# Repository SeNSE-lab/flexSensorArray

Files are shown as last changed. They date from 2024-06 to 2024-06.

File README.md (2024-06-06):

# flexSensorArray
whisking

# Software
Check scripts for the majority of the documentation. 3 scrips are included here:
- **flexSensorArray_control.ino** firmware to be loaded onto an Arduino Mega
- **flexlib.py**  python library that provides an api to control the flex sensor array and read signals. 
designed to be imported into an ipython notebook
- **controller_notebook.ipynb** notebook used to control the experiment. contains examples for using the flex
sensor array. designed to be the software interface for the project

## Arduino Software
It is recommended to install Arduino IDE 2 on your machine, install required 
libraries with the Arduino Library Manager, then upload the flexSensorArray_control.ino 
onto your Arduino Mega  

You should not need to do anything besides load the flexSensorArray_control.ino 
onto your Arduino. The only change to the code I might suggest is to 
reduce the baud rate if you're encountering too many communication errors. Make sure to edit the BAUD_RATE 
in the flexlib file to match if you do  

### Additional Required Libraries
These should all be available in the Arduino Library Manager
- Adafruit_MotorShield
- TimerOne
- AccelStepper

## Python
controller_notebook is designed to be the interface with this project, and 
ideally is the only file that should be edited. You will need to use a local notebook
(i.e. not colab, jupyter notebook recommended) as communication with the Arduino 
occurs via serial.

### Additional Required Libraries
- pyserial
- pandas
- matplotlib (optional but recommended)

# Hardware
## Parts
- Arduino Mega
- [Adafruit Motor Shield V2](https://learn.adafruit.com/adafruit-motor-shield-v2-for-arduino/overview)  and header pins
- 3.3 V, 1.5 or 3 Amp power supply (for 1 or 2 motors respectively)
- [Stepper motor](https://www.moonsindustries.com/p/nema-17-standard-hybrid-stepper-motors/ms17hd6p4150-000004611110008904)
- [Motor shaft coupler](https://www.amazon.com/QCQIANG-Coupling-Coupler-Flanged-Handmade/dp/B09TQM6F17?th=1)
- [Limit switch](https://www.digikey.com/en/products/detail/omron-electronics-inc-emc-div/D2FS-FL-N/4753388)
- [Flex sensor](https://www.adafruit.com/product/1070)
- [Flex sensor clincher connector](https://www.sparkfun.com/products/14195)
- 3D printed whisker
- 3D printed 2-sided whisker bracket
- 3D printed homing tab
- 3D printed motor mount
- ~100 kOhm resistor
- M3 harware
- Various wires and breadboard

## Microcontroller and Motorshield
This project was designed to be run on an Arduino Mega and use
[Adafruit Motorshields V2](https://learn.adafruit.com/adafruit-motor-shield-v2-for-arduino/overview) 
If you are stacking shields, make sure to solder the address bits. When initializing software, pass in 
the integer value of the address pins soldered (e.g. if you solder the two rightmost pins, 
the address would be 3 - 00011 in binary).

Each Arduino can support up to 16 whiskers and up to 16 stacked shields (though only up to a few shields are 
expected to be used). Each shield can support up to 2 stepper motors. 

## Power
The [stepper motors](https://www.moonsindustries.com/p/nema-17-standard-hybrid-stepper-motors/ms17hd6p4150-000004611110008904)
provided are rated for 1.5 amps, and the coils have a resistance of 2.2 ohms. Thus, a 3.3 V power supply 
that can provide 3 amps is recommended if you plan to run 2 motors on one motor shield.
3 amps is also the limit for the motor shields. Be careful of motors overheating and chips on the 
motor shield burning out if you go above 3.3 volts. You can plug power into the Arduino barrel jack 
and put the power jumper on the shield, or hook up power to the power terminal on the motor shield.  

## Wiring
### Arduino and Motor Shield
The Arduino pictured below is wired for 2 motors with 2 whiskers each. Note the order of the colored wires 
connected to the motor shield motor terminals. Whisker outputs should be wired in the order you wish 
them to be referenced starting at A0. Limit pins should be connected in the even numbered pins starting 
at 22. Make sure these are wired in the same order that you initialize the motors. For example, if your 
motor string is '21' and you have 2 whiskers per column, plug the limit pin associated with the
motor connected to second stepper terminal
(M3 and M4) into pin 22 and the limit pin associated with the motor in the first stepper terminal 
to pin 24. Then hook up the whiskers on stepper 2 to A0 and A1 and the whiskers on stepper 1 
to A2 and A3.

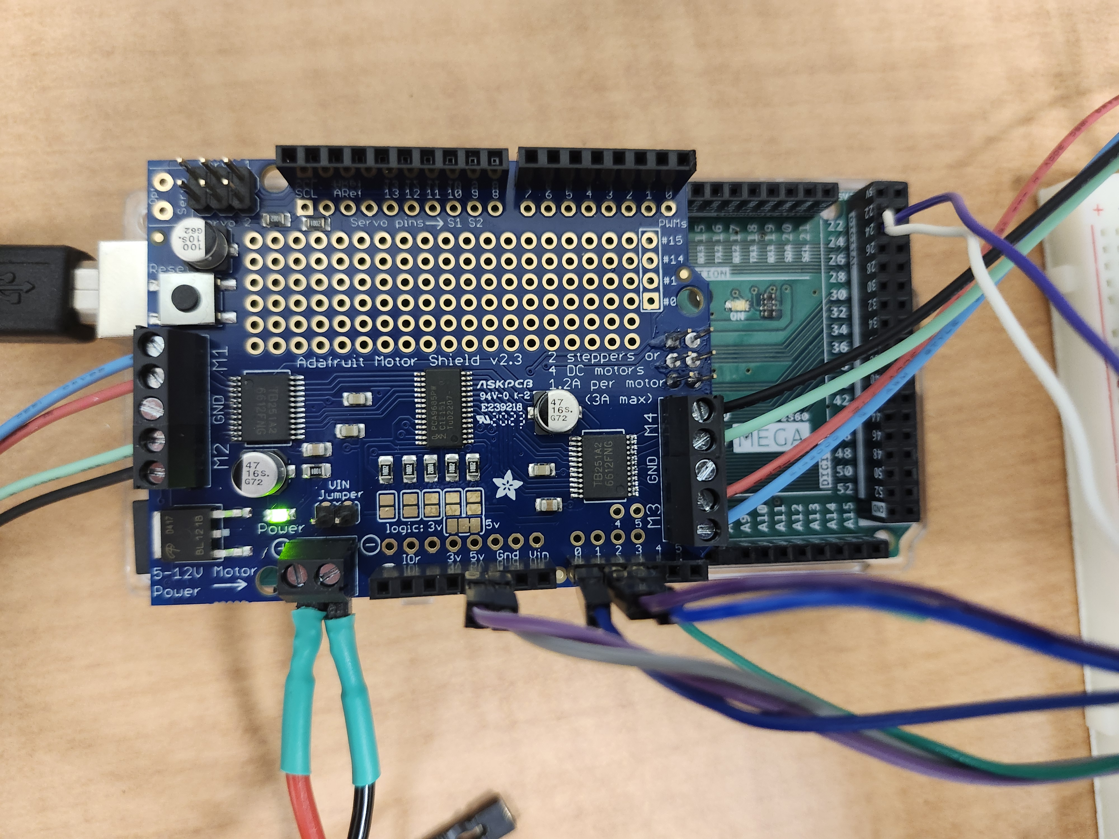
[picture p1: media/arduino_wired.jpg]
arduino_wired


### Whiskers
This project is designed to use a voltage divider circuit to read the signals from the whiskers. 
Wire a resistor between +5V and one end of your whisker sensor. This is your output, also wire it to 
one of the analog pins on the arduino. Wire the other end of the whisker sensor to ground. It may take 
some tuning to figure out the best resistor value to use to get the best signal range without saturating 
the signal. I found around 100 kOhms to be a good value (I used 2 200 kOhm resistors in parallel). 
The flex sensor resistance is about 25 kOhms at rest with resistance increasing as it bends. Note 
that the Arduino is using a reference voltage of 1.1 V for reading the analog signal, so you do not 
want your output voltage to go above 1.1 V.

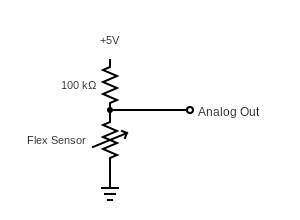
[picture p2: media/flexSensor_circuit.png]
flexSensor_circuit


### Limit Switch
As there is no encoder on the stepper motor, the limit switch is used to find the home/0 steps position of 
the motor. During the homing procedure (which runs during the MotorController.init() function) the stepper 
will rotate until the limit tab triggers the limit switch, then record this position as 0 steps.

The two pins closest to the green button/lever hinge are the active pins on the limit switch. One should 
be wired to one of the even numbered pins starting at 22 on the Arduino, and the other to ground.  

Note that there are two places you may place the limit switch on the 3D printed limit switch holder. One 
is designed to trigger when the whiskers are at "-90°", or parallel to 2 sides of the square motor. The 
other is 72° away from this. Chose whichever best fits your needs, but the default control parameters were 
chosen when using the "72°" slot as shown below.

## Assembly of other components
Image of assembled whisker column:
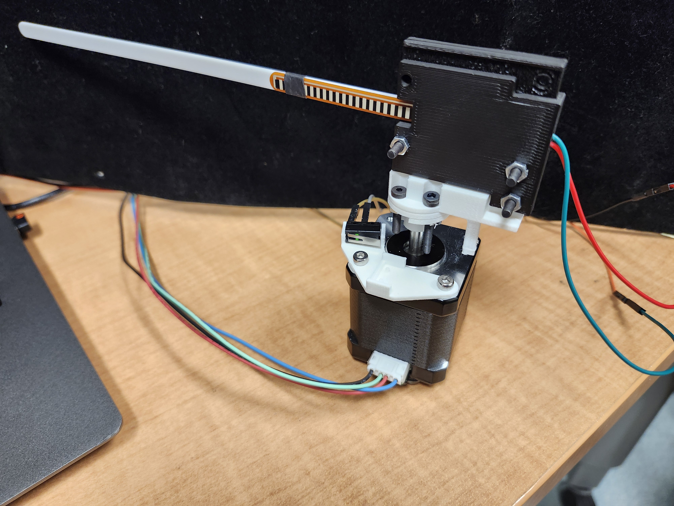
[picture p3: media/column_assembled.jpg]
column_assembled


A few tips:
- All hardware components use M3 screws
- A screw can be removed from the motor housing to allow for the screws holding the limit switch 
holder to be screwed in all the way
- The tip of the flex sensor should be only loosely held by a band, as it needs to slide as the whisker flexes. 
Tape the back of the band if necessary to prevent it from moving along the whisker. Some heat shrink was provided to use as 
this band, apply heat to make it tighter
- Ensure the flex sensor is straight when closing the clincher connector
- The 3D printed motor shaft couplers have a hole that allows you to use an M3 screw as a set screw. I may have made the hole diameter a bit too large
as the set screws easily strip the plastic hole. Try wedging something thin along the 
flat side of the shaft or taping the shaft to tighten the fit if this is a problem. Or try a larger diamter screw if you have one available.

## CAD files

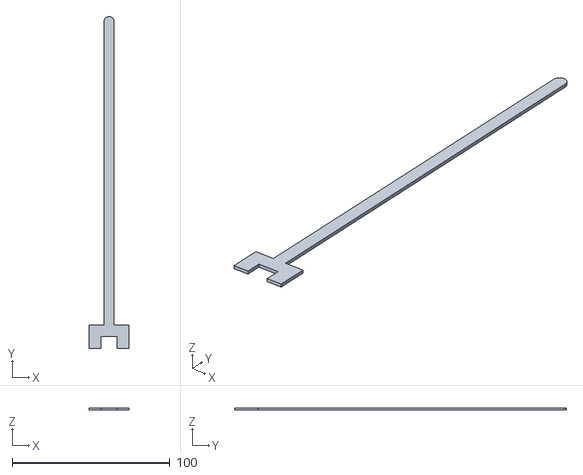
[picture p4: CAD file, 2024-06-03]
CAD/whisker.stl
25.3 x 210.5 x 1.50

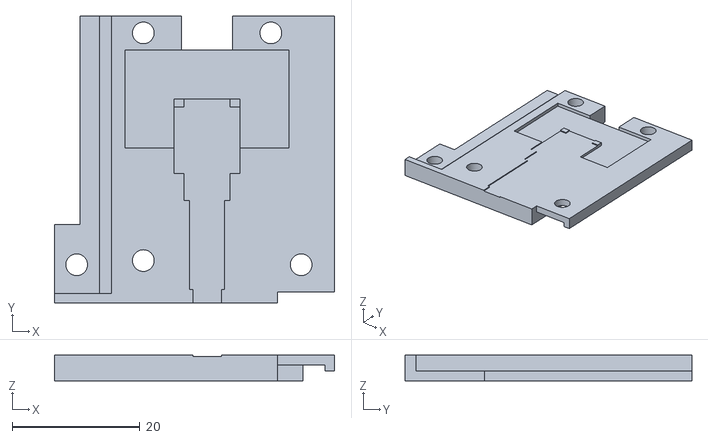
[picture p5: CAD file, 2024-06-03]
CAD/bracket_rear.stl
43.9 x 45.0 x 4.00

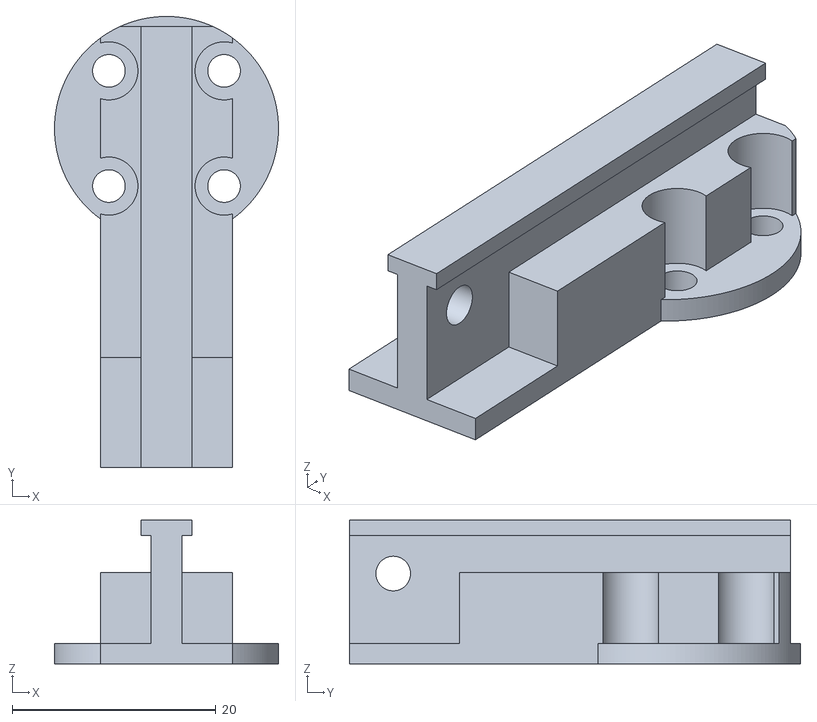
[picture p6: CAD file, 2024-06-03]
CAD/motor_mount.stl
22.0 x 44.3 x 14.1

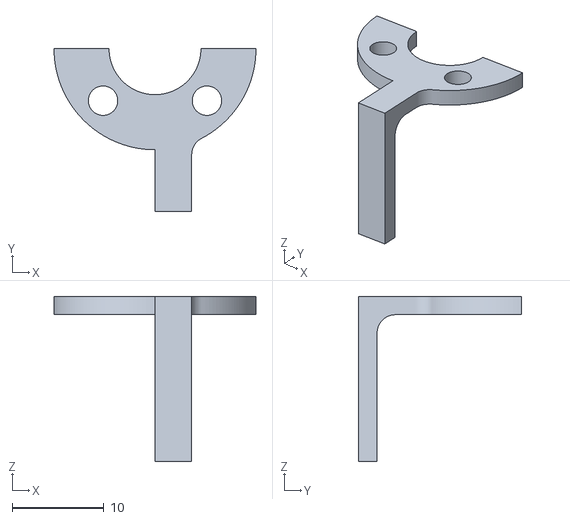
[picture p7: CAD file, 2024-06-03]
CAD/homing_limit_tab.stl
22.0 x 17.7 x 18.0

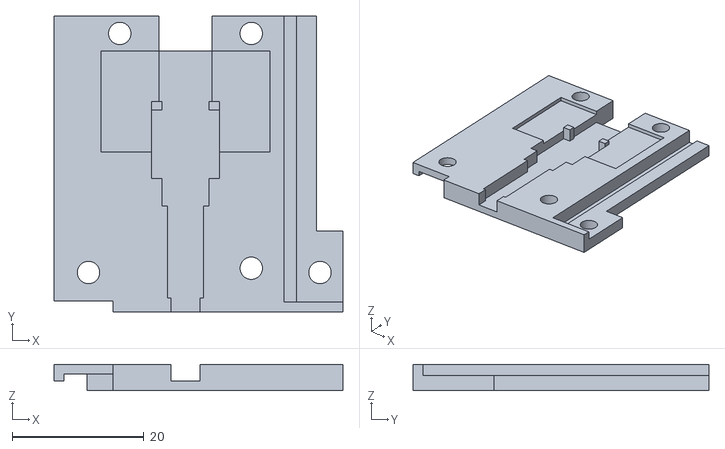
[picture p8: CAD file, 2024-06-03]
CAD/bracket_front.stl
43.9 x 45.0 x 4.00

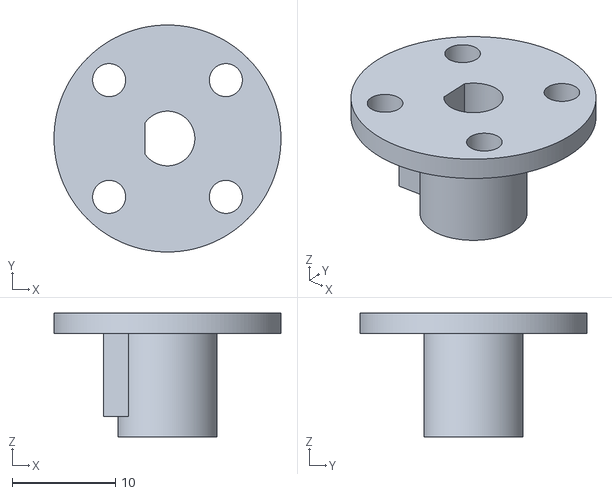
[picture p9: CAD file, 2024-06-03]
CAD/plastic_motor_coupler.stl
22.0 x 22.0 x 12.0

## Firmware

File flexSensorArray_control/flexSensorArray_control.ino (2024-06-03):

#include <Wire.h>
#include <Adafruit_MotorShield.h>
#include "utility/Adafruit_MS_PWMServoDriver.h"
#include <TimerOne.h>
#include <AccelStepper.h>

// Created by Kevin Kleczka May 2024, contact kevin.kleczka@northwestern.edu


////////// Initialize constants
// flag to denote command should be applied to all whiskers/column
#define ALL_FLAG 999

// Serial baud rate, make sure this matches with flexlib.BAUD_RATE
const unsigned long BAUD = 921600;

// Steps per revolution of motor. NOTE: since INTERLEAVE step mode is used, this is double the number of steps per revolution of the motor
const int STEPS_PER_REVOLUTION = 400;

//// hardware addresses
// These are used based on the integer value passed in
//    e.g. if no addr pins are soldered on a shield pass in 0, if the first and second from the right are soldered pass in 3
const uint8_t motorShield_addresses[] = { 0x60, 0x61, 0x62, 0x63, 0x64, 0x65, 0x66, 0x67, 0x68, 0x69, 0x6A, 0x6B, 0x6C, 0x6D,
                                          0x6E, 0x6F, 0x70, 0x71, 0x72, 0x73, 0x74, 0x75, 0x76, 0x77, 0x78, 0x79, 0x7A, 0x7B, 0x7C, 0x7D, 0x7E, 0x7F };
// these will be used in order as new whiskers and motors are added
//  e.g. if you set up 6 whiskers on 2 motors (3 whiskers each) the whisker signals will be read from A0 to A5, and limit pins will be 22 and 24
const int analogPins[] = { A0, A1, A2, A3, A4, A5, A6, A7, A8, A9, A10, A11, A12, A13, A14, A15 };
const int limit_pins[] = { 22, 24, 26, 28, 30, 32, 34, 36, 38, 40, 42, 44, 46, 48, 50, 52 };


// Maximum supported hardware
const int MAX_SHIELDS = 16;
const int MAX_STEPPERS = 16;
const int MAX_WHISKERS = 16;

// Max number of steps allowed to be targeted
const long MAX_STEPS = 200;


////////// Initialize variables
// default step mode
int step_mode = INTERLEAVE;

// pointer arrays for motor control
Adafruit_MotorShield *motor_shields[MAX_SHIELDS];
Adafruit_StepperMotor *steppers[MAX_STEPPERS];
AccelStepper *accel_steppers[MAX_STEPPERS];

// default whisk steps
long default_prot = 133;
long default_ret = 22;

// default accelStepper maxSpeed and acceleration
long default_speed = 1500;
long default_accel = 500;

// set up column parameters
long prot_steps[MAX_STEPPERS] = { default_prot };
long ret_steps[MAX_STEPPERS] = { default_ret };
int is_left[MAX_STEPPERS] = { 0 };
int whisker_col_id[MAX_WHISKERS];
int whisking_status[MAX_STEPPERS] = { 0 };

// init number of connected components
int num_shields = 0;
int num_steppers = 0;
int num_whiskers = 0;

// datastream buffer
long output_buffer[7];
int buff_idx;

// sampling params
volatile int sampling = 0;
unsigned long sampling_period = 20000;

// allocate space for a few variables
int stepper_id;
int status;

// set debug messages for serial monitor debugging
int debug = 0;

//////// Accel stepper setup variables
// I gave up trying to figure out a better way to do this
// Forward and backward stepping functions for each stepper
void forwardStep0();
void backwardStep0();
void forwardStep1();
void backwardStep1();
void forwardStep2();
void backwardStep2();
void forwardStep3();
void backwardStep3();
void forwardStep4();
void backwardStep4();
void forwardStep5();
void backwardStep5();
void forwardStep6();
void backwardStep6();
void forwardStep7();
void backwardStep7();
void forwardStep8();
void backwardStep8();
void forwardStep9();
void backwardStep9();
void forwardStep10();
void backwardStep10();
void forwardStep11();
void backwardStep11();
void forwardStep12();
void backwardStep12();
void forwardStep13();
void backwardStep13();
void forwardStep14();
void backwardStep14();
void forwardStep15();
void backwardStep15();

// Function pointers for stepping functions
typedef void (*StepFunc)();

StepFunc forwardSteps[MAX_STEPPERS];
StepFunc backwardSteps[MAX_STEPPERS];

void initializeSteppers();


//////// Set up command communication protocol
// Number of words (argument variables) in a user command line.
char *argument_words[8];
// Buffer to use for receiving special user-defined ASCII commands.
char user_command_buffer[64];
// Index to use when filling the user command buffer.
uint8_t user_command_buffer_index = 0;
uint8_t c = 0;  // character received
char output_line[71];

void parse(char *line, char **argument_words, uint8_t maxArgs) {
  uint8_t argCount = 0;
  while (*line != '\0') { /* if not the end of line ....... */
    while (*line == ',' || *line == ' ' || *line == '\t' || *line == '\n')
      *line++ = '\0';         /* replace commas and white spaces with 0    */
    *argument_words++ = line; /* save the argument position     */
    argCount++;
    if (argCount == maxArgs - 1)
      break;
    while (*line != '\0' && *line != ',' && *line != ' ' && *line != '\t' && *line != '\n')
      line++; /* skip the argument until ...    */
  }
  *argument_words = '\0'; /* mark the end of argument list  */
}


// Timer1 interrupt service routine
void timerIsr() {
  // prints the current values over serial (ie sends character representations of all values)
  // prints a line for each attached whisker with values in following order:
  //  'timestamp', 'whisker_id', 'stepper_id', 'whisking_status', 'curr_steps', 'sensor_out'
  // NOTE that the millis() interrupt gets paused during handling of this intterrupt, so all whiskers will have the same timestamp
  if (sampling) {

    for (int i = 0; i < num_whiskers; i++) {
      buff_idx = 0;
      // 'timestamp
      output_buffer[buff_idx] = millis();
      buff_idx++;
      // whisker_id
      output_buffer[buff_idx] = i;
      buff_idx++;
      //stepper_id
      stepper_id = whisker_col_id[i];
      output_buffer[buff_idx] = stepper_id;
      buff_idx++;
      // whisking_status
      output_buffer[buff_idx] = whisking_status[stepper_id];
      buff_idx++;
      // curr_steps
      output_buffer[buff_idx] = accel_steppers[stepper_id]->currentPosition();
      buff_idx++;
      // sensor_out
      output_buffer[buff_idx] = analogRead(analogPins[i]);
      buff_idx++;
      for (int j = 0; j < buff_idx; j++) {
        Serial.print(output_buffer[j]);
        Serial.print(' ');
      }
      Serial.println();
    }
  }
}

void home_stepper(int stepper_id) {
  // retract stepper until limit switch is triggered
  while (digitalRead(limit_pins[stepper_id]) == HIGH) {
    if (is_left[stepper_id]) {
      steppers[stepper_id]->onestep(FORWARD, SINGLE);
    } else {
      steppers[stepper_id]->onestep(BACKWARD, SINGLE);
    }
    delay(25);
  }
  accel_steppers[stepper_id]->setCurrentPosition(0);
}



void setup() {

  Serial.begin(BAUD);

  delay(250);

  // let python know we're running
  Serial.println('!');

  // set reference voltage for analog read to 1.1 v to maximize signal range
  analogReference(INTERNAL1V1);

  //////// read setup commands
  // separate command and inputs with spaces ("cmd val1 val2 ...")

  // add shield with steppers and whiskers
  //  s shieldAddr steppersToAdd whiskersPerStepper sideColumnIsOn
  //    for last 3 params first digit is added first, second is added second
  //    e.g. "s 0 12 22 00" adds motor shield with addr 0, adds stepper 1 with 2 whiskers on the right side, then adds stepper 2 with 2 whiskers on the right side
  // set sampling interval in microseconds
  //  p interval
  //    e.g. "p 20000" sets the sample interval to 20,000 microseconds, or 50 Hz
  // complete setup
  //  c
  //    e.g. "c" denotes the setup is complete

  int setup_complete = 0;
  int sidx;
  int midx;
  int numw;
  int side = 0;
  num_whiskers = 0;
  while (!setup_complete) {
    while (Serial.available() > 0) {  // PC communication
      c = Serial.read();
      if (c == '\r') {
        user_command_buffer[user_command_buffer_index] = 0;
        parse((char *)user_command_buffer, argument_words, sizeof(argument_words));

        // add shield with steppers and whiskers
        //  s shieldAddr steppersToAdd whiskersPerStepper sideColumnIsOn
        if (strcmp(argument_words[0], "s") == 0) {
          sidx = atoi(argument_words[1]);
          midx = atoi(argument_words[2]);
          numw = atoi(argument_words[3]);
          side = atoi(argument_words[4]);

          int mone = midx % 10;
          int mten = (midx / 10) % 10;

          int wone = numw % 10;
          int wten = (numw / 10) % 10;

          int sone = side % 10;
          int sten = (side / 10) % 10;


          motor_shields[num_shields] = new Adafruit_MotorShield(motorShield_addresses[sidx]);
          motor_shields[num_shields]->begin();

          if (mten) {
            if (wten) {
              for (int i = 0; i < wten; i++) { whisker_col_id[i] = num_steppers; }
              num_whiskers += wten;
            }
            is_left[num_steppers] = sten;
            steppers[num_steppers] = motor_shields[num_shields]->getStepper(STEPS_PER_REVOLUTION, mten);
            num_steppers += 1;
          }
          if (mone) {
            if (wone) {
              for (int i = 0; i < wone; i++) { whisker_col_id[i] = num_steppers; }
              num_whiskers += wone;
            }
            is_left[num_steppers] = sone;
            steppers[num_steppers] = motor_shields[num_shields]->getStepper(STEPS_PER_REVOLUTION, mone);
            num_steppers += 1;
          }
          num_shields += 1;
        }
        // set sampling interval in microseconds
        //  p interval
        else if (strcmp(argument_words[0], "p") == 0) {
          sampling_period = atoi(argument_words[1]);
        }
        // complete setup
        //  c
        else if (strcmp(argument_words[0], "c") == 0) {
          setup_complete = 1;
        }

        user_command_buffer_index = 0;
      } else if (((c == '\b') || (c == 0x7f)) && (user_command_buffer_index > 0)) {
        user_command_buffer_index--;
      } else if ((c >= ' ') && (user_command_buffer_index < sizeof(user_command_buffer) - 1)) {
        user_command_buffer[user_command_buffer_index++] = c;
      }
    }
  }

  // initialize analog pins to read whisker values
  for (int i = 0; i < num_whiskers; i++) {
    pinMode(analogPins[i], INPUT);
  }
  // initialize limit pins for stepper homing
  for (int i = 0; i < num_steppers; i++) {
    pinMode(limit_pins[i], INPUT_PULLUP);
  }

  // initialize accelSteppers
  initializeSteppers();

  if (debug) Serial.println("setup complete");

  // initialize sampling timer intterupt
  Timer1.initialize(sampling_period);
  Timer1.attachInterrupt(timerIsr);
}
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

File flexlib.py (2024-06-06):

import serial  # install pyserial
import serial.tools.list_ports
import datetime
import time
import os
import pandas as pd
import threading

# Created by Kevin Kleczka May 2024, contact kevin.kleczka@northwestern.edu

# Serial communication baud rate, make sure this matches Arduino BAUD rate
BAUD_RATE = 921600
STEPS_PER_REVOLUTION = 400
ALL_FLAG = 999

KEY_LIST = ['timestamp', 'whisker_id', 'stepper_id', 'whisking_status', 'curr_steps', 'sensor_out']

save_interval = 60  # automatically save log every 60 seconds


class MotorController(object):
    def __init__(self, project_dir=None, title_string=None, exp_tag=None, shield_addrs=None, contact_thresh=100,
                 motor_startup='12', num_whiskers_per_col=2, prot_steps=133, ret_steps=22, sampling_period=20000,
                 push_steps=22, pull_steps=6, palpate_num=3, contact_behavior='palpate'):
        """
        Create motor controller object. Searches for an Arduino connected to a usb port and initializes a serial
        connection. If project_dir is not defined, it will create a directory to store the data log file in the
        current working directory named "yourExpTag_currentDateTime". Sets up a thread to read datastream from
        Arduino. Once streaming has started, the data will be automatically saved every 60 seconds by default. This
        interval can be changed by modifying the save_interval variable in this file. Use MotorController.write_log()
        to manually save the log file. All data will be saved to log dataframe. Additionally, lists containing the
        position of each whisker (in steps) and the voltage of each whisker will be stored in the whisker_steps and
        whisker_vals variables for easy access with format motorController.whisker_vals[whisker_id][sample_idx]


        :param project_dir: Directory to store the experiment data
        :param title_string:    Name of the data log file. Recommended to leave this as None. If not defined, the default
        title string of "expTag_currDateTime" will be used
        :param exp_tag: Name of the experiment. If not defined, will be set to "noExpTag"
        :param shield_addrs:    A list of Adafruit Motorshield addresses that are connected to the Arduino. This should
        be the value of the address bits soldered on the shield converted to an integer. For example, if no addr bits
        are soldered, the vale is 0, if 0b0010 are soldered, the value is 2.
        :param contact_thresh:  The number of whisker signal steps above resting value that constitutes a contact
        :param motor_startup:   A string or list of strings that define which steppers will be used on each shield,
        the order they will be referenced, and the side they belong to. Defaults to right side if sides are not defined.
        For example, '12' will initialize steppers 1 and 2 on the right side and reference stepper 1 first. '2' will
        initialize only motor 2 on the right side. '21rl' will initialize stepper 2 on the right side and stepper 1 on
        the left side, and stepper 2 will be referenced first.
        :param num_whiskers_per_col:    Number of whiskers on each stepper.
        :param prot_steps:  The number of steps from the home position to which the columns will protract during a whisk
        :param ret_steps:   The number of steps from the home position to which the columns will retract during a whisk
        :param sampling_period: The number of microseconds between samples. Testing was done at 50 Hz (20000 us)
        :param push_steps:  How many steps to push past the detected contact point when palpating
        :param pull_steps:  Number of steps before contact location to retract to when palpating
        :param palpate_num: Number of times to palpate after a contact has been detected
        :param contact_behavior:  Set to 'palpate' to palpate when a contact is detected. Nothing else has been
        implemented, so setting it to anything else will just ignore contacts
        """
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
